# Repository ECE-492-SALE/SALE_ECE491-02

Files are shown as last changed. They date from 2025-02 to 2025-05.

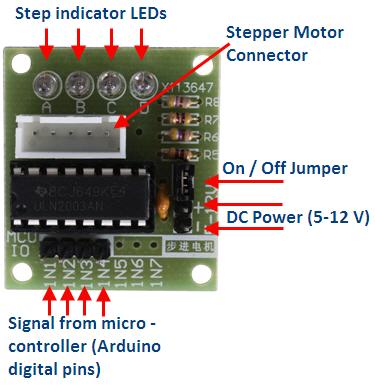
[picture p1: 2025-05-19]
Smart Pill Box/Schematic/UNL2003-board.jpg

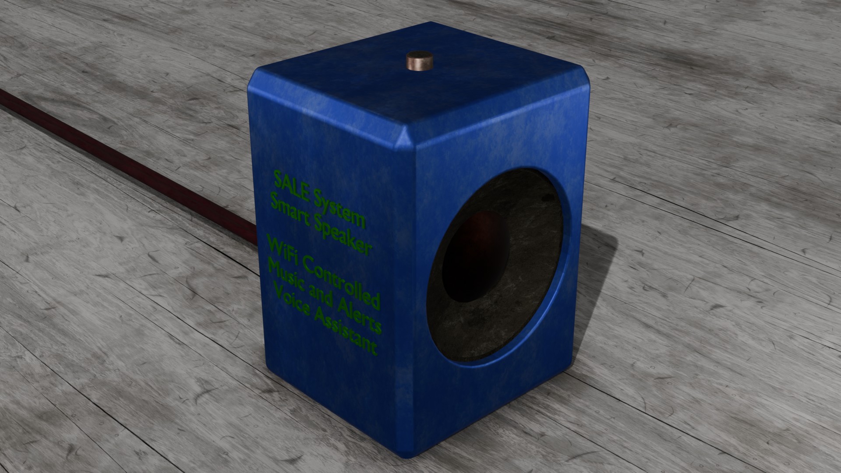
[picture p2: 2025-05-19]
SmartSpeaker/SmartSpeakerRender3.jpg

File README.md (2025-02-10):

# SALE_ECE491-02
Smart Assistive Living Environment (SALE) Senior Design project at Lafayette College

## Setup

### If you're downloading this on a new device, follow these steps

Open a Developer PowerShell from the Start Menu using the Start->All apps- >Raspberry Pi Pico SDK v1.5.5->Pico – Developer PowerShell I also suggest that you right-click on this menu entry and select “Pin to Start” for faster access in the future.

cd into your Documents folder

Run the following commands:
```bash
mkdir pico
cd pico
git clone -b master https://github.com/raspberrypi/pico-sdk.git
cd pico-sdk 
git submodule update --init 
cd .. 
git clone -b master https://github.com/raspberrypi/pico-examples.git
git clone https://github.com/priskillaw/SALE_ECE491-02.git
```

## Before making any changes, follow these steps

Open a Developer PowerShell 

cd into SALE_ECE491-02

Run "git pull"

You can start working now. Open Pico - Visual Studio Code

## To run things
```bash
cd build 
cmake -G "NMake Makefiles" .. 
nmake
```

Reboot the pico, then drag and drop the .uf2 file from the build file into the pico in file explorer

## To push things
cd into SALE_ECE491-02
```bash
git add Folder_Name
git commit -m "message/notes"
git push
```

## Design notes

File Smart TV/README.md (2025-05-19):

# Setting up the Smart TV

These instructions assume you already have a Roku set up on your TV.

1. Follow the steps in the [Getting started with your Raspberry Pi Pico W](https://projects.raspberrypi.org/en/projects/get-started-pico-w/0) guide to:
   - Install MicroPython onto the Pi Pico W
   - Set up the Thonny Python IDE

2. Download [`main.py`](https://github.com/ECE-492-SALE/SALE_ECE491-02/blob/main/Smart%20TV/main.py).

3. Open main.py in Thonny and edit the **Internet Credentials** section in the code to include:
   - Your Wi-Fi credentials
   - Your Roku device's IP address

4. Save the modified program to your Pico:
   - Go to `File` > `Save As` > `Raspberry Pi Pico`
   - Ensure the file name is exactly `main.py`
   - You may need to overwrite the existing `main.py` file

> **Note:** Naming the file `main.py` ensures the program starts automatically when the Pico receives power.

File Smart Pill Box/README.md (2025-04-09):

# Raspberry Pi Pico W Home Assistant Starter Project Using `arduino-pico`

I'm pretty excited about Pico W: it's such a reliable, high-quality board and each one costs just $6 (if you can find one).

I'm building an IoT project with Pico W and Home Assistant, and it took weeks of research and experimentation to figure out the basics of integration of all the necessary components. This starter pulls together everything I've learned so you can get to building quickly.

Fill out `src/Credentials.h`, upload to your Pico W, then you'll have a working integration that allows you to toggle the Pico W's board LED from the Home Assistant dashboard. From this starter you'll have a solid foundation to build your own custom device in a private, local Intranet of Things.



This readme will provide pointers to everything you'll need. Let me know if it's missing anything!

## Dependencies

- [Raspberry Pi Pico W](https://www.raspberrypi.com/products/raspberry-pi-pico/?variant=raspberry-pi-pico-w), a $6 microcontroller board with WiFi
- [PlatformIO](https://platformio.org/platformio-ide), an extension for [VSCode](https://code.visualstudio.com) with the most robust and reliable Arduino developer experience
- [`arduino-pico`](https://github.com/earlephilhower/arduino-pico): a community-developed Arduino core for Pico/Pico W and other RP2040 boards with constant updates and excellent support for existing Arduino code
- [`arduino-home-assistant`](https://github.com/dawidchyrzynski/arduino-home-assistant): a thorough Arduino/Home Assistant integration using MQTT

## Getting started

---
### Prerequisites
- PlatformIO set up in VSCode
- Home Assistant and MQTT broker accessible on the WiFi network your Pico W is joining (see appendix below for guidance on setup)
- HA MQTT integration with discovery enabled (this is the default/recommended behavior, so unless you turned it off, you're probably good to go)
---

1. Hold the `BOOTSEL` button on your Pico W while connecting it via USB
2. Open this project in VSCode
3. Edit `src/Credentials.h` with:
```
  - WiFi SSID
  - WiFi Password
  - MQTT Username
  - MQTT Password
  - MQTT Broker IP
```
4. Select the PlatformIO sidebar tab and choose Project Tasks > Upload and Monitor
5. Once the project logs a connection to the MQTT broker, open your Home Assistant instance
6. From Settings > Devices and Services, find the MQTT card and click the link that says `X devices`
7. From the resulting list, select `Pico W HA Starter`
8. Under the **Controls** heading you should see `Board LED`. Toggle the switch to turn your green board LED on and off



That's it. Now you've got a working example integration of all the pieces needed to communicate between an inexpensive, high-quality microcontroller and Home Assistant, all happening on your local network.

See the [examples in `arduino-home-assistant`](https://github.com/dawidchyrzynski/arduino-home-assistant/tree/main/examples) for additional components you can easily integrate, including sensors, buttons, even HVAC controls.

# Troubleshooting

- To come

# Appendix: Setting up a local Home Assistant installation with Mosquitto

## Home Assistant install

Home Assistant can be [installed](https://www.home-assistant.io/installation/) several ways on all kinds of hardware. Raspberry Pi is a popular choice, but you can also use your existing computer for initial explorations. *Home Assistant Container* is probably the quickest and most portable way to get started, whichever hardware you're using, though this does mean you'll have to manage some add-ons yourself, including MQTT.

## MQTT and Mosquitto

MQTT provides realtime messaging between devices in a network. The [Eclipse Mosquitto](https://github.com/eclipse/mosquitto) project offers a server that can act as an _MQTT broker_, a central hub for MQTT devices to send and receive data.

If you're using **Home Assistant Operating System**, check these instructions to [install the Mosquitto MQTT broker add-on](https://github.com/home-assistant/addons/blob/master/mosquitto/DOCS.md).

If you're using **Home Assistant Container**, [this tutorial](https://hometechhacker.com/mqtt-home-assistant-using-docker-eclipse-mosquitto/) provides a great overview on how to set up and secure Mosquitto in a seperate container.

Once your MQTT broker is enabled, [add the MQTT integration to your Home Assistant instance](https://www.home-assistant.io/integrations/mqtt/).

# Pull requests

PRs are welcome on these points:

- Enhance documentation (especially any troubleshooting steps you found helpful)
- Refine project structure
- Additional code paths to accommodate common variations (unsecured MQTT broker, different WiFi authentication, etc)
- Fix my bad C++

The goal of the project is to provide enough example structure to allow developers to add complexity without making a messy, crowded `main.cpp` file. PRs that simplify down to a single file probably won't be merged. If you have ideas on how to make this an even better foundation for building complex IoT projects, I'm all ears.

---

Questions? Comments? Gripes? Open an [issue](https://github.com/daniloc/PicoW_HomeAssistant_Starter/issues/new/choose) if you think there will be general interest or impact on the project. Otherwise hit me up: [mail@danilocampos.com](mailto:mail@danilocampos.com).

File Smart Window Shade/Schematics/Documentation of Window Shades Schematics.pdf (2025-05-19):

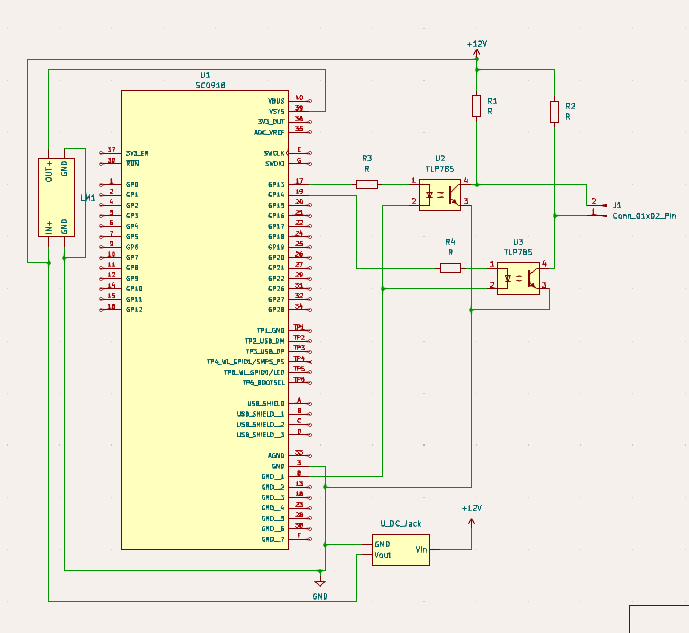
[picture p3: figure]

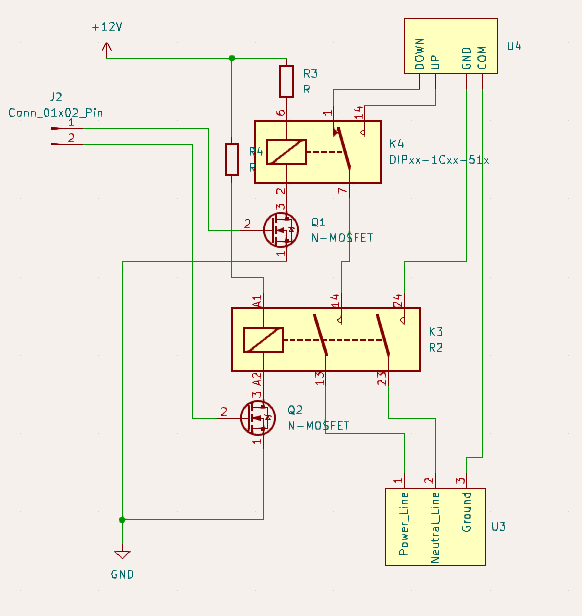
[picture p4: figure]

New Revisions made 02/09/2025: Changed layout of power distribution from the 12 to 5 volt converter.

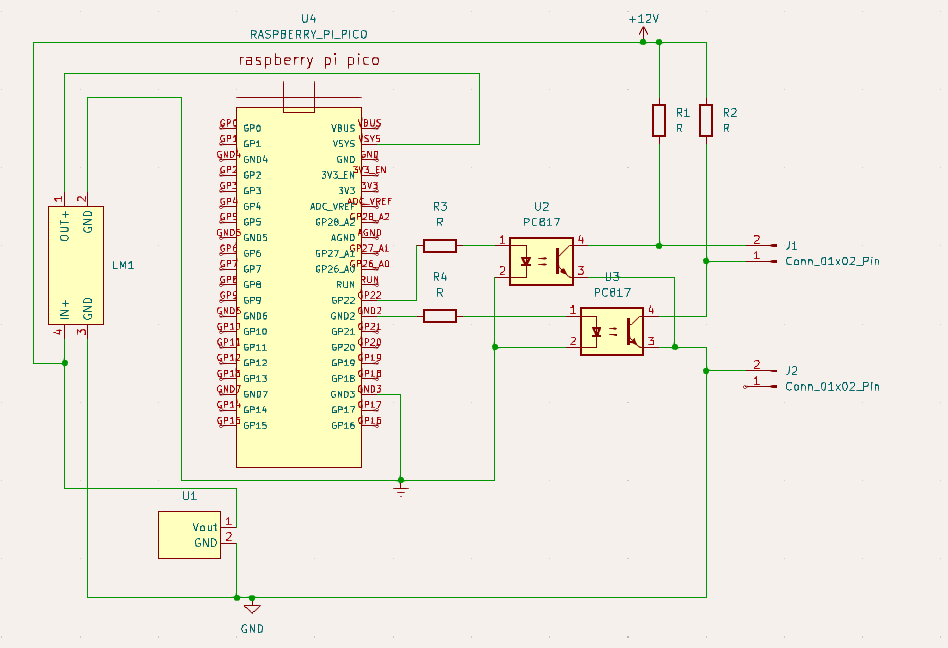
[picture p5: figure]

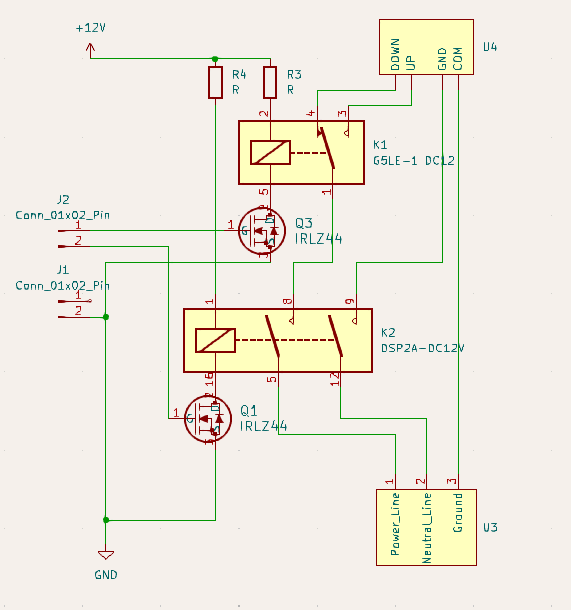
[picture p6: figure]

New revisions made 02/12/2025: Adjusted resistors to one schematic from the other, switched transistors, and fixed schematic layout. The resistors in this schematic are as follows: R1=180k, R2=200k, R3 & R4 = 10k.

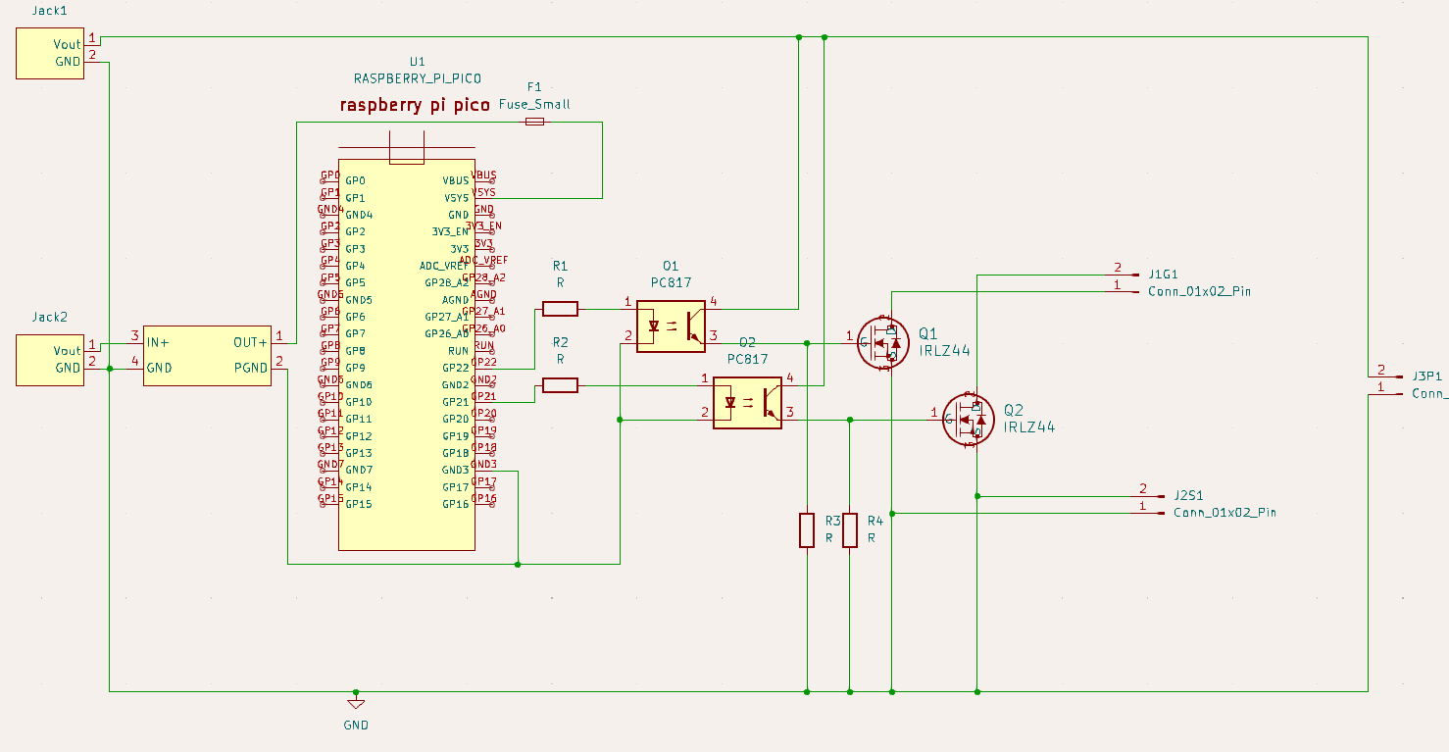
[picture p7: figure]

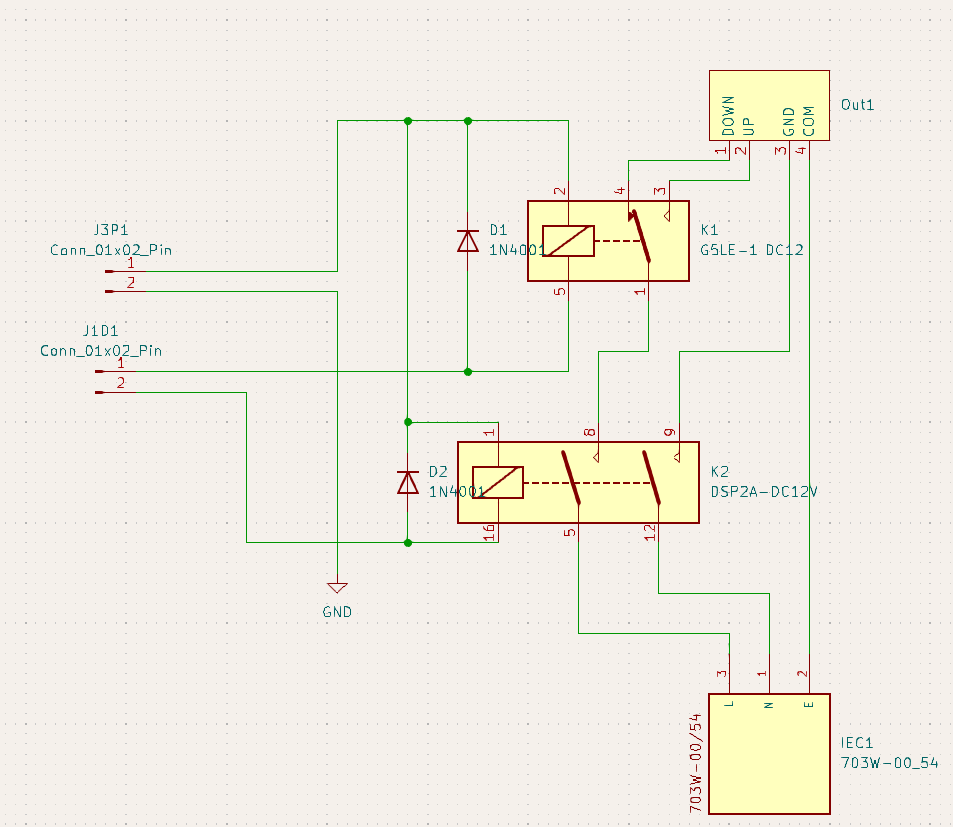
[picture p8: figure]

New revisions made 02/15/2025: Adjusted placement of resistors and their values as follows: R3=180k, R4=200k, R1 & R2 = 10k. Also, implemented fly back diodes to prevent unwanted voltage spikes.

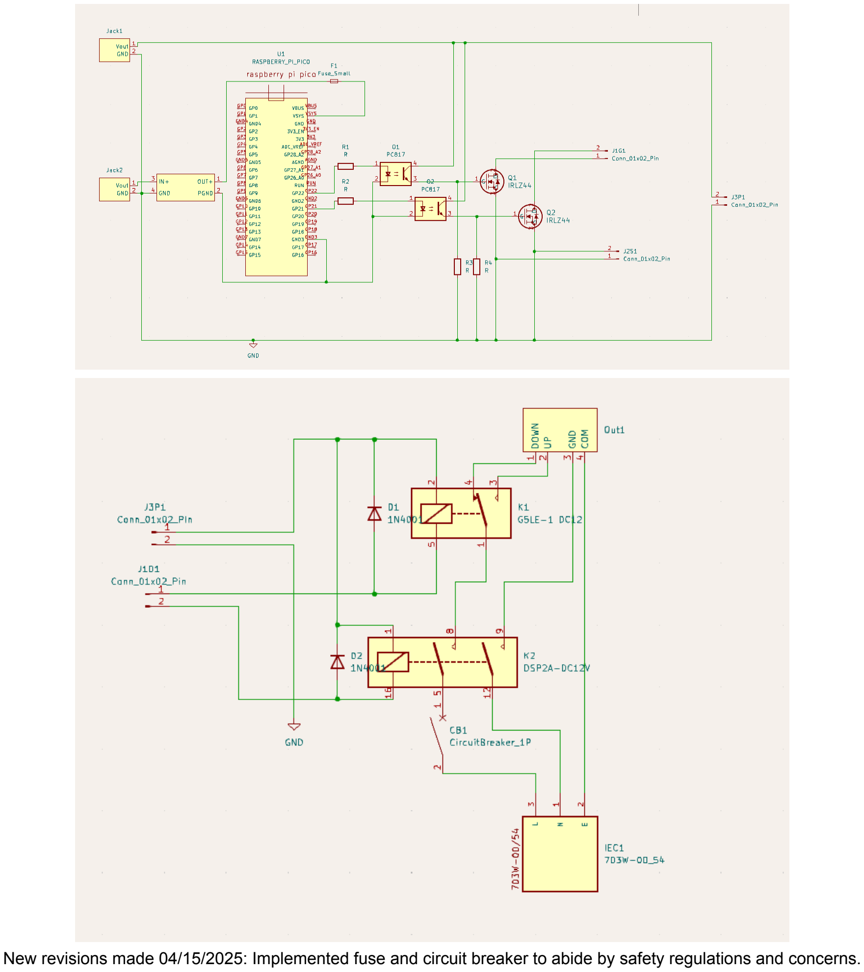
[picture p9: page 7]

New revisions made 04/15/2025: Implemented fuse and circuit breaker to abide by safety regulations and concerns.

The system design is divided across two separate PCBs: one dedicated to power distribution and the other to the microcontroller. This separation provides electrical isolation between the DC power and AC power domains, enabling safe and effective motor control. The Raspberry Pi Pico W microcontroller communicates with the central hub using the MQTT protocol, facilitated by the ArduinoHA library. This allows the device to be controlled through the Home Assistant (HA) web interface.

Wiring:

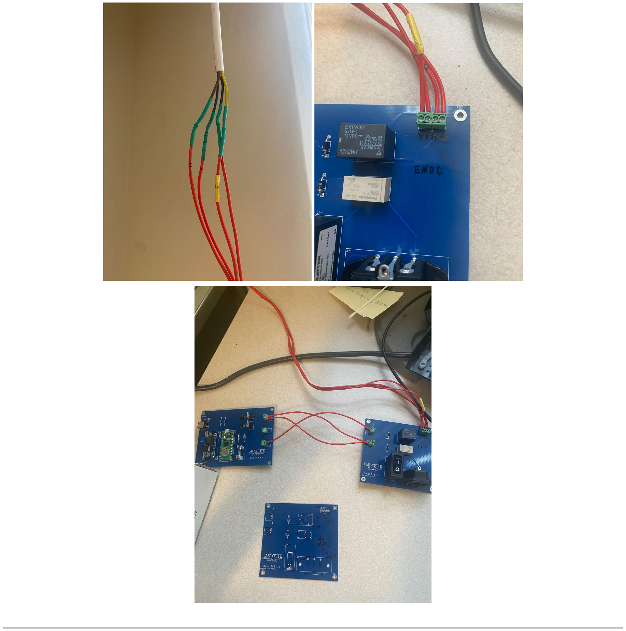
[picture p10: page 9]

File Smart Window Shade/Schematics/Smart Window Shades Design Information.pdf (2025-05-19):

What is it?

The Smart Window Shades is a window shade controller that is designed for residents to control their window blinds through the kick buttons and a smart mobile device UI interface. The
window shade consists of various components, such as the motor, a PCB (high voltage) that controls power to the window shade control system, and another PCB (low voltage) that controls communication with the hub.

What is the structure?

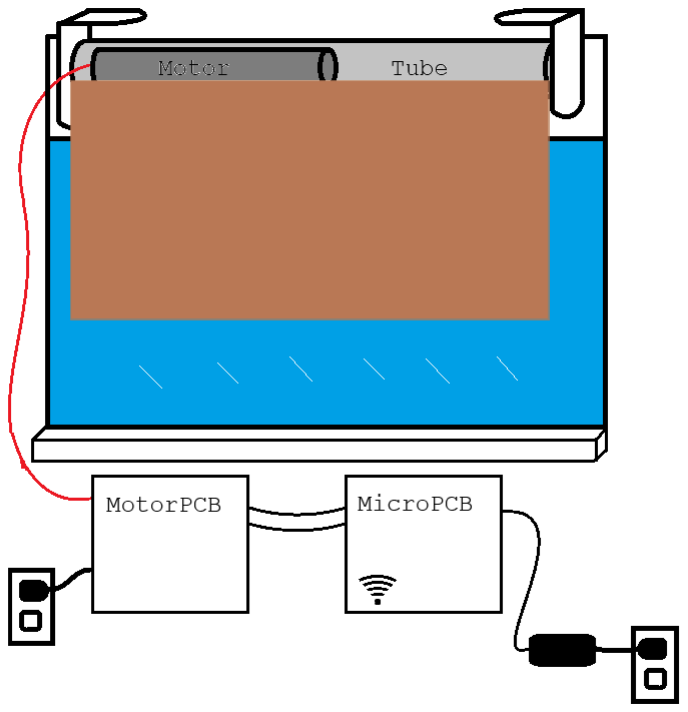
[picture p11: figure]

How does it work?

The main function of the device is to simply operate a motor up and down. It completes this function with the use of two PCBs, one with power distribution from a wall outlet and another with a microcontroller that will communicate with the hub and allow for control of the overall device. The power distribution PCB, or the MotorPCB, utilizes relays to switch on and off the motor as well as the direction of the motor, and hence the shades. Meanwhile, the MicroPCB uses DC 12V as power and sends signals to the MotorPCB through wired connections to switch the relays.

The microcontroller, Raspberry Pi Pico W, utilizes PlatformIO and C++ as the compiler and code language. The Pico W communicates with the hub through Wi-Fi using the MQTT protocol. It uses the ArduinoHA library to communicate automation functions with the HUB 1. (https://dawidchyrzynski.github.io/arduino-home-assistant/index.html)

Sources

1- ArduinoHA documentation- link (https://dawidchyrzynski.github.io/arduino-home-assistant/index.html)

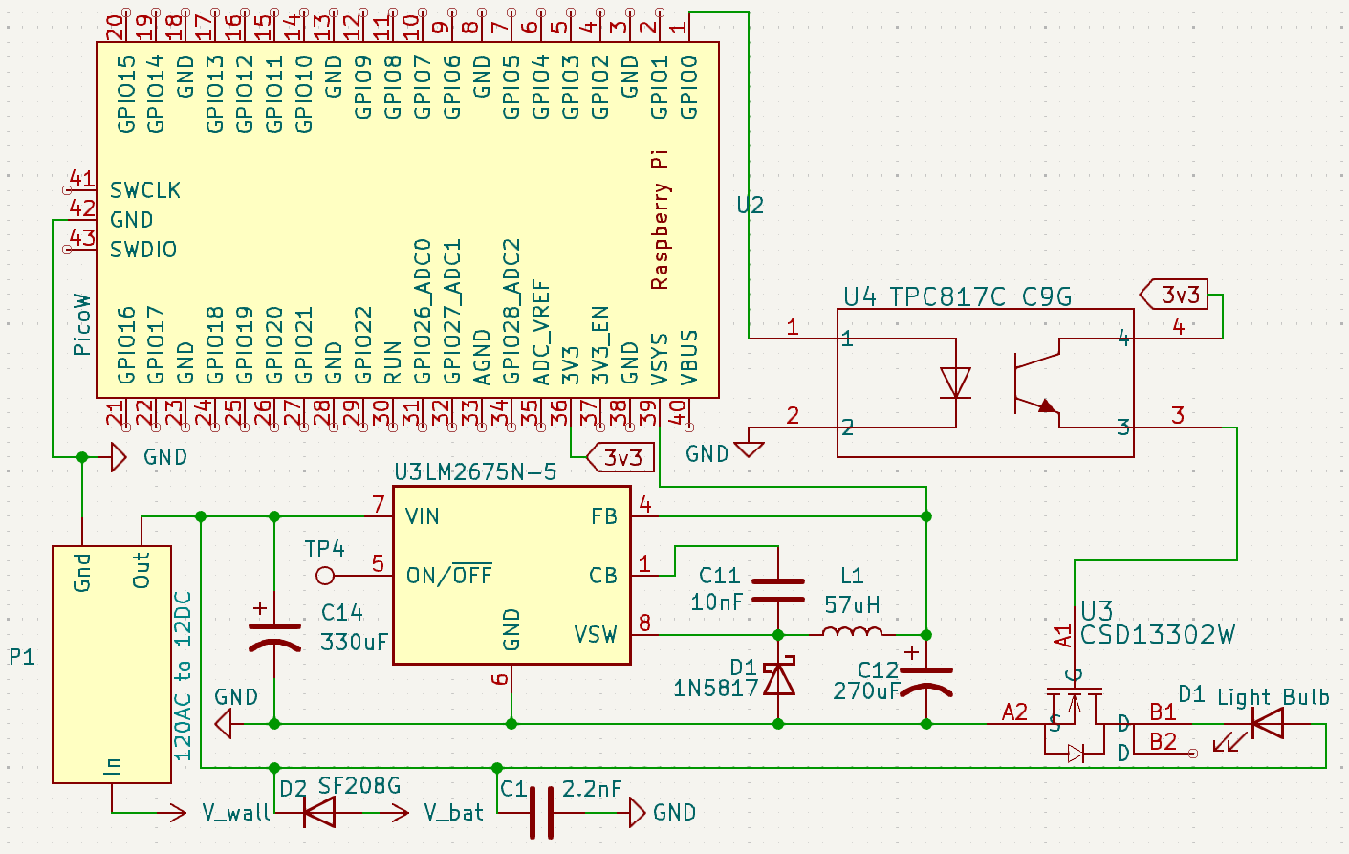
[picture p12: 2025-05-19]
Smart Light/Schematic/CircuitImage.png

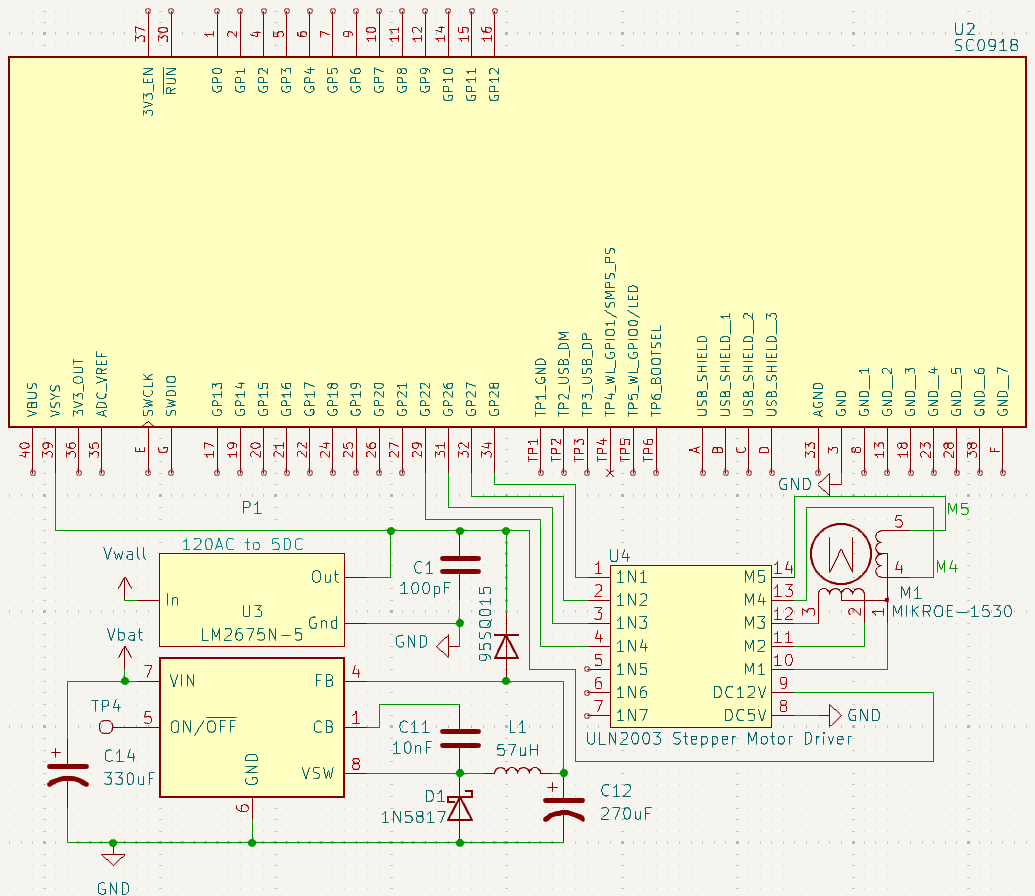
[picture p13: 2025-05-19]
Smart Pill Box/Schematic/CircuitImage.png

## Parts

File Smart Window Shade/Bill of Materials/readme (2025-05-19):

Please refer to the Window Shade Bill of Materials for money spent on device development.

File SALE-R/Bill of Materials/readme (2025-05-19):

Please refer to the SALE-R Bill of Materials for money spent on device development.

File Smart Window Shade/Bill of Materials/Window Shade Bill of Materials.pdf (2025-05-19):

Quantity | Cost Desc. | Part Number | Part Description | Link to Product | Per Unit | Total Per Item
1 | each | | 12V DC Adapter | https://www.amazon.com/Facmogu-Connector-5-5x2-5mm-5-5x2-1mm-Transformer/dp/B09BQBWKKT $14.39 | | $14.39
1 | each | | Power Cord | https://www.amazon.com/dp/B072BYGKZZ | $6.86 | $6.86
2 | each | 255-1052-ND | DSP2A-DC5V 5V Relay Non-Latch DPST-NO(2 Form A) | https://www.digikey.com/en/products/detail/panasonic-electric-works/DSP2A-DC5V/251824 $5.29 | | $10.58
2 | each | Z1014-ND | G5LE-1 DC5 5V Relay Non-Latch SPDT(1 Form C) | https://www.digikey.com/en/products/detail/omron-electronics-inc-emc-div/G5LE-1-DC5/280368 $1.84 | | $3.68
2 | each | 255-1053-ND | DSP2A-DC12V 12V Relay Non-Latch DPST-NO(2 Form A) | https://www.digikey.com/en/products/detail/panasonic-electric-works/DSP2A-DC12V/251825 $6.28 | | $12.56
2 | each | Z1015-ND | G5LE-1 DC12 12V Relay Non-Latch SPDT(1 Form C) | https://www.digikey.com/en/products/detail/omron-electronics-inc-emc-div/G5LE-1-DC12/280366 $1.70 | | $3.40
1 | each | | LM2596 Buck Converter | https://www.amazon.com/Maxmoral-Converter-Adjustable-Step-Down-Regulator/dp/B07MKQXNWG $7.99 | | $7.99
1 | pack of 10 | | DIP-4 PC817C PC817 opto isolator | https://www.amazon.com/MEETOOT-Transistor-Optocoupler-Mounting-Photoelectric/dp/B0BZY8NPLZ $4.99 | | $4.99
1 | each | 703W-00/54 | AC Power Entry Modules PCB | https://www.digikey.com/en/products/detail/qualtek/703W-00-54/245561 $2.02 | | 2.02
2 | each | 58-TIL197X-ND | TIL197X Optosiolator | https://www.digikey.com/en/products/detail/isocom-components-2004-ltd/TIL197X/21184649 $1.080 | | $2.160
2 | each | FOD852300-ND | FOD852300 Optoisolator | https://www.digikey.com/en/products/detail/onsemi/FOD852300/1054006 $1.140 | | $2.280
10 | each | WM7770-ND | 2 Position Terminal Block Header | https://www.digikey.com/en/products/detail/molex/0395021002/1280621 $0.459 | | $4.590
1 | each | | 120V Electric Tubular Motor for Roller Shades | https://www.ebay.com/itm/113835892439?chn=ps&norover=1&itemid=113835892439&targetid=4580771614098651&device=c&mktype=&googleloc=&poi=&campaignid=603247547&mkgroupid=1234752552191001&rlsatarget=pla-4580771614098651&abcId=9316119&merchantid=51291 $140.380 | | $140.380
1 | each | 486-1632-ND | 4435.0004. circuit breaker | https://www.digikey.com/en/products/detail/schurter-inc/4435-0004/1576911?s=N4IgTCBcDaICxwMwFYB0AGTcQF0C%2BQA $16.570 | | $16.570
10 | each | 1N4001 | Diode | https://www.digikey.com/en/products/detail/diotec-semiconductor/1N4001/13164614 $0.073 | | $0.730
10 | each | 486-1172-ND | 751.0062, Fuse Clip 10 A 1 Circuit Cartridge Through Hole | https://www.digikey.com/en/products/detail/schurter-inc/0751-0062/1522971?s=N4IgTCBcDaIAwHYCsBGAdHOA2CBdAvkA $0.219 | | $2.190
5 | each | 5923-5ST400-R-ND5ST 400-R, FUSE GLASS 400MA 250VAC 5X20MM | | https://www.digikey.com/en/products/detail/bel-fuse-inc/5ST-400-R/1009014 $0.346 | | $1.730
10 | each | 277-1721-ND | Screw Terminal (2 pos) | https://www.digikey.com/en/products/detail/phoenix-contact/1984617/950849 $0.620 | | $6.200
1 | set of 5 | | Hernan_Tovar-MicroPCB-Gerber Files | | $9.100 | $9.100
1 | each | | 50mm Tube | https://www.aliexpress.us/item/2255800674929877.html?spm=a2g0o.productlist.main.69.68243c481ZdaQA&algo_pvid=15d34c6a-c3b3-4ebb-8017-95513a388cc9&algo_exp_id=15d34c6a-c3b3-4ebb-8017-95513a388cc9-34&pdp_ext_f=%7B%22order%22%3A%2216%22%2C%22eval%22%3A%221%22%7D&pdp_npi=4%40dis%21USD%218.08%215.66%21%21%2158.06%2140.64%21%402103244417417945778375013e710d%2110000009689232526%21sea%21US%210%21ABX&curPageLogUid=lSyqkVcQup2B&utparam-url=scene%3Asearch%7Cquery_from%3A&gatewayAdapt=glo2usa $15.040 | | $15.040
1 | each | | 50mm Tube Aliexpress Shipping (88.5% ≤ 15 days) | | $25.200 | $25.200
1 | each | Window Shade Cloth - 8x12ft | https://www.amazon.com/Shatex-Fabric-Sun-Block-Pergola-Vertical/dp/B0152638SC?crid=1F482N8GGBAL4&dib=eyJ2IjoiMSJ9.0UGw9fhsERxLAzTZLdW-JWIaOosoAo99veP5jVaRUsiY2D-IYwChbElyhkwkbPCLwDlF8RiHA2zShFba4dmbsUE518HGo6yW3qHcKo2unuJsxlZyP4cbEDyOchVSCSaZ_oQqpo7o0g4_KozOwEVsKYBbmsE1sUZbhrxUdmricc5waIAYOgvM7MPXfemQZp8r2P_yj_VbM_mmKQ-Z8iuHsFjxTMo1GycocEaOXfID_1Qkm3uDPHZP1Ln6CnfGGQ0my2wNWTUSEMKE6iaxYibsJGw_EuJyJuGPgF2Owds7DlNpPoJbha8ORG1NZniMUqEv3o7y6jIYL9mhtwYntKwfBSfl49S7hAqa5w8ozXxaJbd4RB7oNQVJvZcE7Gi1dnUwq1M6zdff-pdXaC-OYXHisOYX2cvZJqxRhrCS96zi21_myYwA3JuHQC6_7cziRtPF.PTbvPzUGwK8BUv7smSho9WjuU2KZ9PW01qAZRnOhmMo&dib_tag=se&keywords=shade%2Bfabricroll&qid=1742962712&sprefix=shade%2Bfabricrol%2Caps%2C327&sr=8-16&th=1 $25.930 | $25.930
1 | each | Heat Shrink Kit | https://www.amazon.com/Ginsco-580-pcs-Assorted-Sleeving/dp/B01MFA3OFA $6.990 | $6.990
2 | each | Clear Scratch Acrylic Sheet, 12" x 12" x 5/64" | https://www.mcmaster.com/products/acrylic-plastic/plastic-1~/clear-scratch-and-uv-resistant-acrylic-sheets-and-bars/ $5.420 | $10.840
| | | Grand Total | $336.40

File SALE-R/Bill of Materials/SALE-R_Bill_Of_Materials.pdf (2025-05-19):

Quantity | Cost Desc. | Part Number | Part Description | Link to Product | Per Unit | Total Per Item
1 | group of 10 | Z12567-ND | Omron EESX3173 Optical Switch https://www.digikey.com/en/products/detail/omron-electronics-inc-emc-div/ee-sx3173-p2/9695331 $18.910 | | | $18.91
5 | each | Z8289-ND | Switch Cable | https://www.digikey.com/en/products/detail/omron-electronics-inc-emc-div/EE-5002-1M/8124128 (https://www.tti.com/content/ttiinc/en/apps/part-detail.html?partsNumber=EE-5002%201M&mfgShortname=OMR&msclkid=a04ac9077cad10313c51ae0e2bbb2bc2) $4.954 | | $4.95
5 | each | 497-4226-5-ND | Voltage Regulator | https://www.digikey.com/en/products/detail/stmicroelectronics/L7805ABP/725181?utm_adgroup=Integrated%20Circuits&utm_source=bing&utm_medium=cpc&utm_campaign=Dynamic%20Search_EN_RLSA&utm_term=integrated%20circuits&utm_content=Integrated%20Circuits&utm_id=bi_cmp-384476624_adg-1299622969467348_ad-81226484852599_dat-2333026235351130:aud-807631101:loc-190_dev-c_ext-_prd-&msclkid=30f93d07fe0513298ca15a0ea9756c5f $1.260 | | $6.30
10 | each | 296-1391-5-ND | Op amp - LM324N | https://www.digikey.com/en/products/detail/texas-instruments/LM324N/277627 $0.238 | | $2.38
10 | each | 754-1615-ND | RGB LED - WP154A4SUREQBFZGC https://www.digikey.com/en/products/detail/kingbright/WP154A4SUREQBFZGC/3084119?utm_adgroup=&utm_source=google&utm_medium=cpc&utm_campaign=PMax%20Shopping_Product_Medium%20ROAS%20Categories&utm_term=&utm_content=&utm_id=go_cmp-20223376311_adg-_ad-__dev-c_ext-_prd-3084119_sig-CjwKCAjwmaO4BhAhEiwA5p4YLyAk4I2ltCuXI3pE9Z9ASIh5VV7s5-rz4vQWj1uRPWmAPOnopJJF7xoCr4cQAvD_BwE&gad_source=1&gclid=CjwKCAjwmaO4BhAhEiwA5p4YLyAk4I2ltCuXI3pE9Z9ASIh5VV7s5-rz4vQWj1uRPWmAPOnopJJF7xoCr4cQAvD_BwE $1.224 | | | $12.24
10 | each | BC548BTACT-ND | Transistor (NPN) - BC548BTA https://www.digikey.com/en/products/detail/onsemi/BC548BTA/4553029?utm_adgroup=&utm_source=google&utm_medium=cpc&utm_campaign=PMax%20Shopping_Product_Medium%20ROAS%20Categories&utm_term=&utm_content=&utm_id=go_cmp-20223376311_adg-_ad-__dev-c_ext-_prd-4553029_sig-CjwKCAjwmaO4BhAhEiwA5p4YL67t7TMbeoZEc35zGVffhJ3N9crvRZnu1P-3F3I7a8i8qWXRaVbQNBoCnBMQAvD_BwE&gad_source=1&gclid=CjwKCAjwmaO4BhAhEiwA5p4YL67t7TMbeoZEc35zGVffhJ3N9crvRZnu1P-3F3I7a8i8qWXRaVbQNBoCnBMQAvD_BwE $0.124 | | | $1.24
10 | each | 1727-4115-1-ND | AND Gate - 74LVC1G08GV,125 https://www.digikey.com/en/products/detail/nexperia-usa-inc/74LVC1G08GV-125/1231422?utm_adgroup=Integrated%20Circuits&utm_source=bing&utm_medium=cpc&utm_campaign=Dynamic%20Search_EN_RLSA&utm_term=integrated%20circuits&utm_content=Integrated%20Circuits&utm_id=bi_cmp-384476624_adg-1299622969467348_ad-81226484852599_dat-2333026235351130:aud-807631099:loc-190_dev-c_ext-_prd-&msclkid=98d76569372a198b0c1c0242ff174319 $0.089 | | | $0.89
1 | each | TO-1127CS | TO-1127CS - 302/304 Stainless Steel Torsion Springs | Century Spring… https://www.centuryspring.com/shop/to-1127cs | | $8.780 | $8.78
1 | each | TO-1052CS | TO-1052CS - 302/304 Stainless Steel Torsion Springs | Century Spring… https://www.centuryspring.com/shop/to-1052cs | | $16.520 | $16.52
1 | each | TO-5074LSCS | TO-5074LSCS - 302/304 Stainless Steel Torsion Springs | Century… https://www.centuryspring.com/shop/to-5074lscs | | $6.360 | $6.36
5 | each | N71179212 | Omron Electronic Components EE-5002 https://us.rs-online.com/product/omron-electronic-components/ee-5002-1m/71179212/ $5.620 | | | $5.62
2 | each | OPB355T | Optical Interrupter | https://www.digikey.com/en/products/detail/tt-electronics-optek-technology/OPB355T/1636794?s=N4IgTCBcDaIPIAUBCBmArGgKiAugXyA $4.130 | | $8.26
1 | each | SUNLU | SUNLU 3D Printer Filament 1.75mm, 1kg Spool, Transparent PLA https://www.amazon.com/SUNLU-Filament-Transparent-Dimensional-Accuracy/dp/B07ZNG4L9P $18.990 | | | $18.99
1 | set of 5 | PCB | Gerber_KB_2025_Kaushik_Padmanabh https://drive.google.com/file/d/1kJjDtBSBimDMkwyHZpLCwrizQ20GpJf3/view?usp=drive_link $11.200 | | | $11.20
1 | each | Foot Rest | Foot Rest | https://www.amazon.com/EHO-Footrest-Washable-Ergonomic-Position/dp/B0CDPNHPX1 $48.820 | | $48.82
5 | each | EE-5002 1M | Switch Cable | https://www.digikey.com/en/products/detail/omron-electronics-inc-emc-div/ee-5002-1m/8124128 $3.786 | | $18.93
10 | each | 754-1615-ND | RGB LED - WP154A4SUREQBFZGC https://www.digikey.com/en/products/detail/kingbright/WP154A4SUREQBFZGC/3084119 $1.760 | | | $17.60
10 | each | BC548BTACT-ND | Transistor (NPN) - BC548BTA https://www.digikey.com/en/products/detail/onsemi/BC548BTA/4553029 $0.162 | | | $1.62
4 | each | 1727-4115-1-ND | AND Gate - SN74LS08N | https://www.digikey.com/en/products/detail/texas-instruments/SN74LS08N/277279 $0.740 | | $2.96
15 | each | 277-1721-ND | Screw Terminal (2 pos) | https://www.digikey.com/en/products/detail/phoenix-contact/1984617/950849 $0.598 | | $8.97
15 | each | 277-1722-ND | Screw Terminal (3 pos) | https://www.digikey.com/en/products/detail/phoenix-contact/1984620/950850 $0.651 | | $9.77
1 | each | Pi Pico | Raspberry Pi Pico WH - Pico Wireless with Headers Soldered https://www.adafruit.com/product/5544 | | $7.000 | $7.00
1 | each | Wire 25FT | 20 Gauge 5 Conductor Electrical Wire 25FT https://www.amazon.com/Conductor-Electrical-Stranded-Extension-Automotive/dp/B0CFJWSHKD $16.990 | | | $16.99
| | | | | Grand Total | $255.30

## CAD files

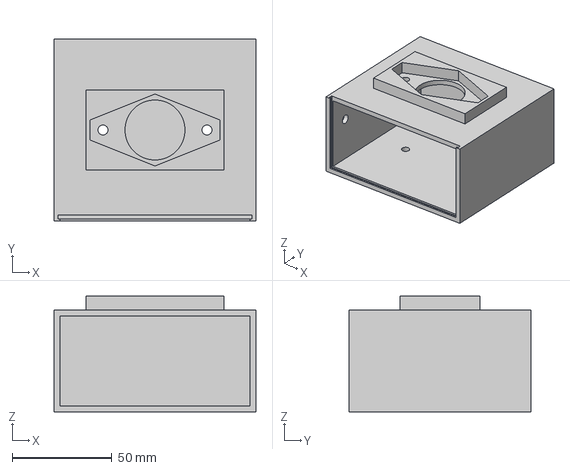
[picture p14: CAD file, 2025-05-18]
Smart Light/3D Print Files/carusoc_ece492_lighthousing.3mf
101.0 x 91.0 x 58.0 mm

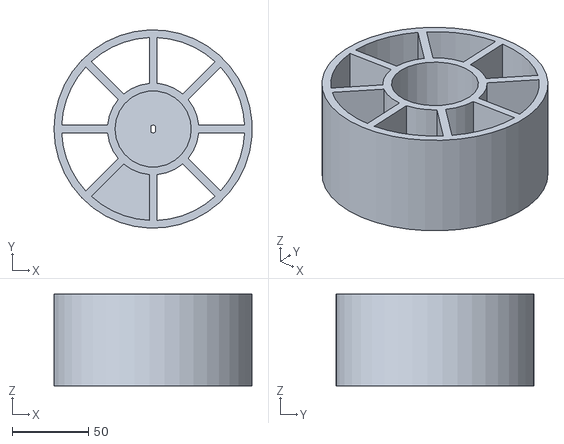
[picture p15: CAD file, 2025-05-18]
Smart Pill Box/3D Print Files/Pill+Box+Wheelv4.obj
129.8 x 129.9 x 60.0

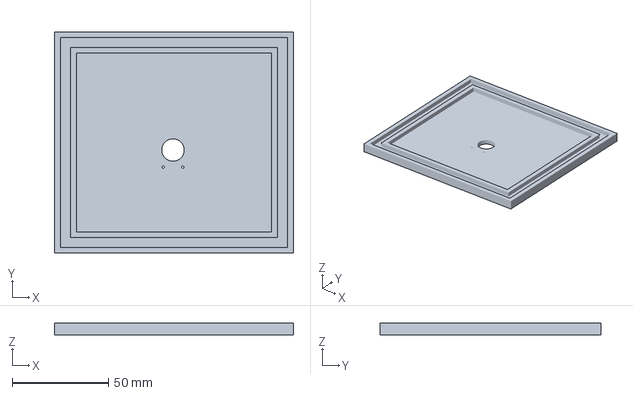
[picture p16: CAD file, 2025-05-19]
SmartSpeaker/3D Print Files/SmartSpeakerCaseTop.3mf
124.4 x 115.0 x 6.00 mm

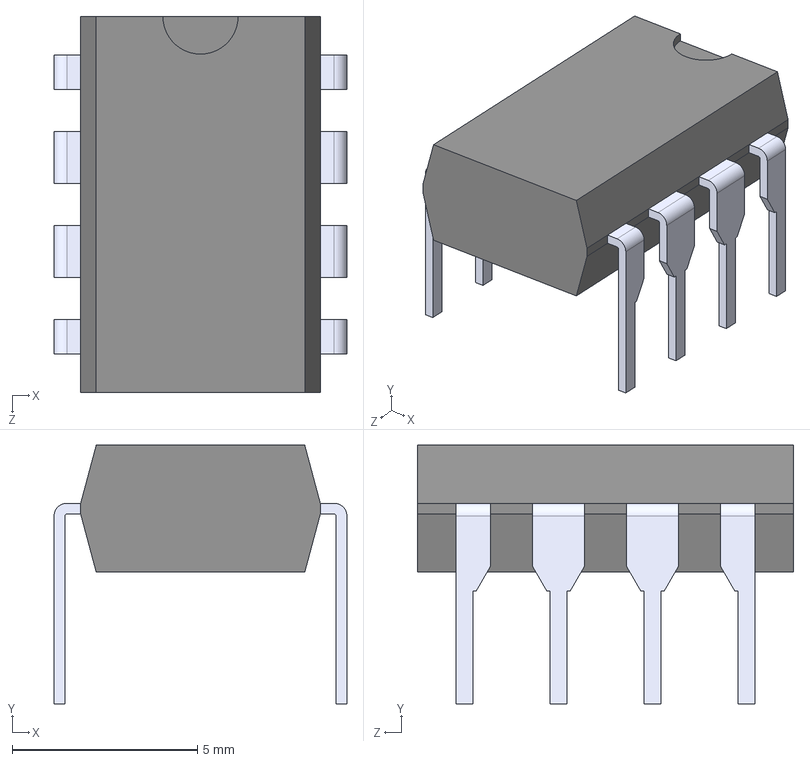
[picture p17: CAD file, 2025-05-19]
SmartSpeaker/Speaker/LTC1655CS8_TRPBF/LTC1655CN8_PBF.step
7.91 x 6.98 x 10.2 mm

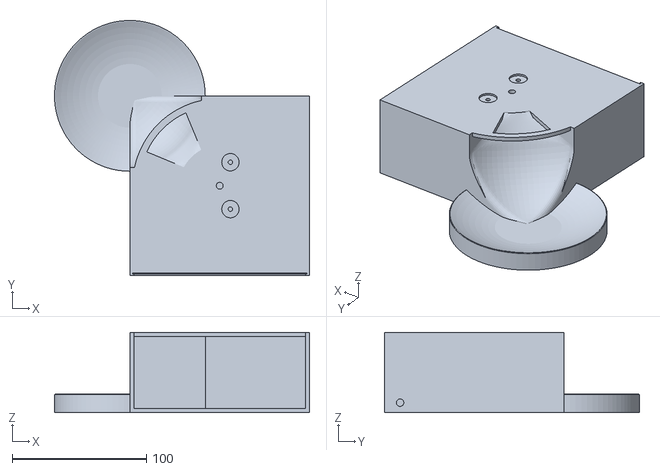
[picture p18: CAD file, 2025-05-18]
Smart Pill Box/3D Print Files/Pill Box Housing v3.stl
190.2 x 190.2 x 60.0

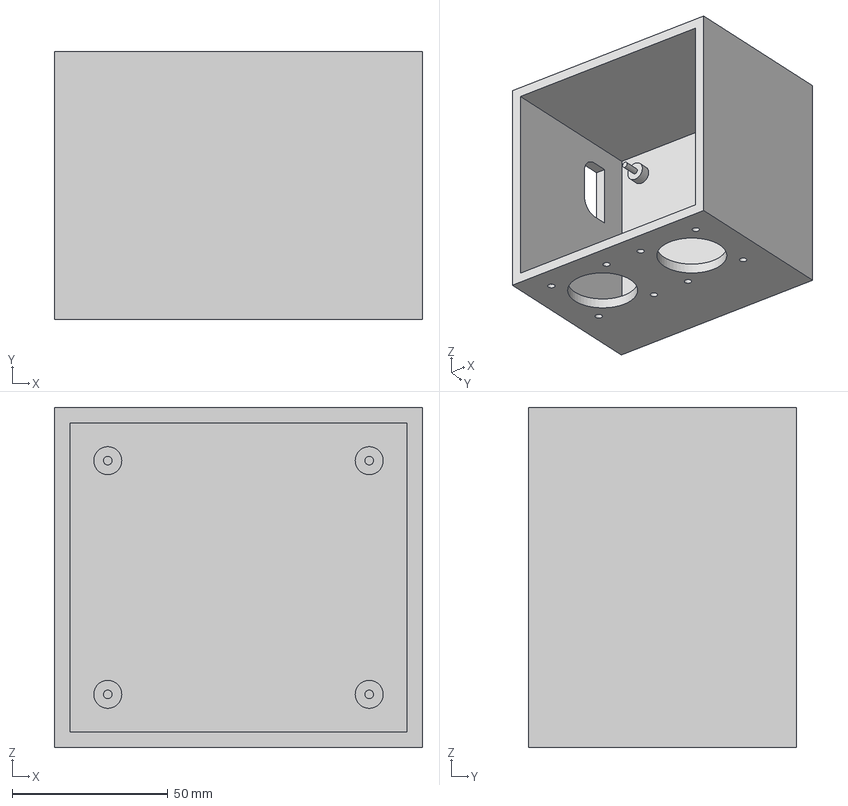
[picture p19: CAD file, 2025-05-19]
SmartSpeaker/3D Print Files/SmartSpeakerCase_Body.3mf
118.0 x 86.0 x 109.1 mm

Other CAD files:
SALE-R/3D Print Files/Bottom+V3.f3d
SALE-R/3D Print Files/Bottom+V4.f3d
SALE-R/3D Print Files/Hinge+Rods.f3d
SALE-R/3D Print Files/Kick-Button+Combined+Visual.f3z
SALE-R/3D Print Files/Top+V4.f3d
Smart Door/3D Print Files/Camera+Holder.f3d
Smart Window Shade/3D Print Files/Shades+PCB+Holder+#1.f3d
Smart Window Shade/3D Print Files/Shades+PCB+Holder+#2.f3d
SmartSpeaker/3D Print Files/speaker+structure+lid.f3d
SmartSpeaker/3D Print Files/speaker+structure.f3d

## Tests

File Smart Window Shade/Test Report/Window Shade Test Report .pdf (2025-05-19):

# Window Shade Test Report

############################################################################## Overall Summary: Window Shades are functional

Tested by: Hernan Tovar, Padmanabh Kaushik. Nicholas Sorak.
Date: 05/3/2025
Report Uploaded 5/19/20205 by Hernan Tovar-Molina ##############################################################################

Mechanical Design Requirements
Test T1: Interaction with Motor
- Equipment: Motor, relays, power supply, and wall outlet.
- Method: Apply a line voltage source switching via protoboard with relays attached, using 12 volts to switch on and off.
- Pass/Fail Criteria: Motor rotates once the voltage applied to the relays is high.

Test T2: Breaker Component
- Test Equipment: Built PCB, breaker.
- Test Method: Switch on/off the breaker component.
- Acceptance Criteria: Disables power to the motor, and motor doesn’t rotate.
Cover Requirements: Wired aspects shall be secured and out of reach/away from the resident.

Test T3: Window Shades Reach
- Test Equipment: Motor, built PCBs, shades.
- Test Method: Enable the motor to spin to its maximum, adjust as necessary.
- Acceptance Criteria: The shades reach to the bottom of the window.

Test T4: Accommodation of PCBs
- Test Method: Insert the PCBs into their designated 3d printed compartments. Check for proper fit, alignment, and secure positioning.
- Acceptance Criteria: The PCBs should fit securely within their housing, with no movement or obstruction.
- Test Equipment: 3D Fusion, ruler.

Cover Requirements: Wired aspects shall be secured and out of reach/away from the resident.

Electrical functionality
Test T5: Voltage Convertor Voltage Regulation
- Test Equipment: Digital multimeter or oscilloscope.
- Test Method:
- Measure the output voltage from the LM 2596 buck converter under both idle and active states.
- Repeat the test under different load conditions(turning the system on or off).
- Acceptance Criteria: The voltage supplied to the microcontroller output side should not exceed 5.1 V.

Test T6: Relay Circuit Current Limitation
- Test Equipment: Digital multimeter
- Test Method:
- Power the GPIO pins from the Pico W and measure the current flowing through the circuit under standard and maximum operating conditions.
- Measure the current in voltage across the drain and source from each transistor and calculate the current.
- Acceptance Criteria: The coil current in the Relays should be ≤ 25 mA and ≤ 33.3 mA, for the DSP2A-DC12V and the G5LE-1 DC12, respectively in all tested conditions.

Test T7: GPIO Input Voltage Limitation to Microcontroller
- Test Equipment: Digital multimeter or oscilloscope.
- Test Method:
- Measure the voltage at the GPIO input pin on the microcontroller in both idle and active states.
- Test under various input signal conditions to ensure stability.
- Acceptance Criteria: The voltage at the GPIO input should not exceed 3.8 V.

Wi-Fi Integration Functionality:

Test T8: Microcontroller Readings
- Test Equipment: Computer and Oscilloscope.
- Test Method:
- Verify if the name of the device appears on the console of the Hub.
- Monitor one of the GPIO pins on the microcontroller while the up cover option from the Home Assistant is pressed.
- Program the microcontroller to turn on the built-in LED if the button is pressed.
- Acceptance Criteria: The microcontroller should register a logic high or logic low signal depending on when the up or down, and stop is pressed.
Cover Requirements: Smart Window Shades shall be connected with the Smart Hub wirelessly.

System level integration (involves 5 buttons):

Setup:
- Attached the motor and tube with shades to the ceiling.
- Wired and connected both of the PCBs to power and each other.

Test T9: Control from HA website.
- Test Equipment: Computer
- Test Method: Use the Home Assistant website to control the shades
- Press either up or down arrows and the stop buttons.
- Acceptance Criteria: Window shades respond accordingly and further verified with audio feedback from the relay.
Test T10: Control from SMD interface.
- Test Equipment: Smart Mobile Device
- Test Method: Use the user interface on the SMD to control the shades.
- Press the arrows, up or down and stop.
- Acceptance Criteria: Window shades respond accordingly and further verified with audio feedback from the relay.
Test T11: Control from SALE-Remote buttons.
- Test Equipment: Kick Buttons

- Test Method: Navigate the user interface on the SMD by using the kick buttons to control the shades.
- Press the respective kick buttons; up, down or stop.
- Acceptance Criteria: Window shades respond accordingly and further verified with audio feedback from the relay.
T9-T11_Cover Requirements:
- The resident shall be able to raise/lower the Smart Window Shades by interfacing with the Smart Mobile Device.
- Simple controls; with a push/touch shall open or close.

Test Result Summary

Test No. | Pass/Fail
T1 | Pass
T2 | Pass
T3 | Pass
T4 | Pass
T5 | Pass
T6 | Pass
T7 | Pass
T8 | Pass
T9 | Pass
T10 | Pass
T11 | Pass

##################################End of report################################

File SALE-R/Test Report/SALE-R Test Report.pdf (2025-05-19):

# SALE-R Test Report

##################################################################################### Overall Summary: Kick Buttons are fully functional

Tested by: Padmanabh Kaushik, Nick Sorak, Scott Torzewski
Date: 5/1/2025
Report Uploaded: 5/19/2025 by Padmanabh Kaushik #####################################################################################
- Mechanical Design Requirements
- Test T1: Interaction with Optical Switch Surface (T1)
i. Method: Visually inspect and measure the clearance between the metal strap and the surface of the optical switch in all button positions using a caliper or other precision measuring tool.
ii. | Acceptance Criteria: There should be a minimum clearance of 1 mm between
| the metal strap and the optical switch surface in both pressed states.
iii. | Observation from Test: The clearance was 2mm between the strap and the
| optical switch, for buttons in the compressed state.
iv. | Pass/Fail: Pass
- Test T2: Laser Interruption upon Button Press (T2)
i. Method: Press the button and observe the optical switch output using a voltmeter
| to confirm that the laser is interrupted by the metal strap.
ii. | Acceptance Criteria: The laser should be fully interrupted once the button is
| pressed.
iii. | Observation from Test: The laser is fully interrupted when the button is pressed,
| as voltage goes down to 0V.
iv. | Pass/Fail: Pass
- Test T3: Laser Continuity in Equilibrium Position (T3)
i. Method: Place the button in its equilibrium position and monitor the optical
| switch output using a voltmeter.
ii. | Acceptance Criteria: The laser should remain uninterrupted in the unpressed
| state.
iii. | Observation from Test: The voltage does not change across the optical switch
| circuit when the button is not pressed.
iv. | Pass/Fail: Pass
- Test T4: Button Return to Equilibrium Position (T4)

i. Method: Manually press the button multiple times and observe whether it reliably returns to its original position. Use a caliper if needed to confirm alignment.
ii. | Acceptance Criteria: The button must return to its equilibrium position after
| every press.
iii. | Observation from Test: The button returns to its original position.
iv. | Pass/Fail: Pass
- Test T5: LED Circuitry Accommodation (T5)
i. Method: Insert the LED driving circuitry into its designated compartment and
| check for secure fit and unobstructed placement.
ii. | Acceptance Criteria: The circuitry must fit securely within the button housing
| with no movement or interference.
iii. | Observation from Test: The LED board fits properly within the button. Each
| LED circuit has dimensions of 2cm x 3cm.
iv. | Pass/Fail: Pass
- Electrical Functionality
- Test T6: Optical Switch Voltage Regulation (T6)
i. Method: Use a multimeter or oscilloscope to measure voltage supplied by the
| Buck Convertor regulator to the optical switch in both idle and active states,
| under various load conditions.
ii. | Acceptance Criteria: Voltage must not exceed 5.5 V.
iii. | Observation from Test: TThe output voltage was 5.2 V.
iv. | Pass/Fail: Pass
- Test T7: LED Driver Circuit Current Limitation (T7)
i. Method: Power the LED circuit and measure current across the 300-ohm source
| resistor using a multimeter. Test under standard and maximum base current
| conditions.
ii. | Acceptance Criteria: Current must remain ≤ 40 mA in all tested conditions.
iii. | Observation from Test: The maximum observed current per button was 38mA..
iv. | Pass/Fail: Pass
- Test T8: GPIO Input Voltage Limitation to Microcontroller (T8)
i. Method: Measure voltage at the GPIO input pin during idle and active states
| using a multimeter or oscilloscope.
ii. | Acceptance Criteria: Voltage must not exceed 3.8 V.
iii. | Observation from Test: The voltage at GPIO was 3.29 V.
iv. | Pass/Fail: Pass
- Individual Button Functionality
- Test T9: Microcontroller Readings (T9)
i. Method: Monitor GPIO pin on the microcontroller while pressing the button.
| The onboard LED should be programmed to turn on when a high signal is
| received.

ii. | Acceptance Criteria: The microcontroller must detect a logic high when the
| button is pressed.
iii. | Observation from Test: The microcontroller detects logic high when button is
| pressed.
iv. | Pass/Fail: Pass
- Test T10: LED Illumination on Button Press (T10)
i. Method: Press the button and visually verify that the button’s LED lights up and
| remains on while pressed.
ii. | Acceptance Criteria: LEDs must illuminate immediately when the button is
| pressed.
iii. | Observation from Test: LED lights up immediately when button is pressed.
iv. | Pass/Fail: Pass
- Test T11: Bluetooth Message Transmission on Button Press (T11)
i. Method: Pair the microcontroller with a tablet or computer. Monitor the
| receiving application or terminal to confirm transmission of
| “buttonName_Pressed” and default “buttonName_!Pressed” messages.
ii. | Acceptance Criteria: An “buttonName_Pressed” message must be sent when
| the button is pressed. “buttonName_!Pressed” must be sent when no button is
| pressed.
iii. | Observation from Test: The button press messages were transmitted properly,
| and were verified by displaying them on smart Mobile Device.
iv. | Pass/Fail: Pass
- System Level Integration (involves 5 buttons)
- Setup:
i. Power the button system (5 buttons and the circuitry) using a 12 V supply
ii. | Place the 5 buttons on a custom mount/footrest that is comfortable to use when a
| person is in a wheelchair.
- Test T12: Button State Detection and String Composition (T12)
i. Test Method: Use a USB connection to print serial output from the
| microcontroller while pressing each button individually and in combinations;
| confirm that the generated string accurately reflects the state of each button.
ii. | Acceptance Criteria: The generated string accurately reflects the current state of
| each button in the format "ON_1 OFF_2…" etc.
iii. | Observation from Test:.The generated string accurately reflected the current
| state of each button in the format "ON_1 OFF_2…" etc.
iv. | Pass/Fail: Pass
- Test T13: Bluetooth Transmission of Button States (T13)
i. Test Method: Pair a tablet or computer with the microcontroller via Bluetooth,
| then press buttons individually and in combinations while monitoring the
| received string in a logging application; verify that each transmission matches the
| current button states and test for consistency under rapid presses.

ii. | Acceptance Criteria: The tablet consistently receives the correct button state
| string for every combination of presses, in the specified format (e.g., Left
| pressed, Right pressed, etc.).
iii. | Observation from Test:. The button presses were detected in tight format. For
| instance Left pressed when the left button was pressed and vice versa..
iv. | Pass/Fail: Pass
- Test T14: Stability and Responsiveness Testing (T14)
i. Test Method: Use logging software to monitor transmitted strings while rapidly
| pressing buttons in different sequences, including simultaneous inputs; observe
| whether the system consistently updates the string without missing or
| misreporting button states.
ii. | Acceptance Criteria: The system should not miss any button press events or
| provide incorrect button states
iii. | Observation from Test: The system detects buttons pressed properly, even when
| they are pressed pretty fast. This is valid as long as button presses are within 0.25
| sec, which is the sampling time programmed in the controller.
iv. | Pass/Fail: Pass
| Test Result Summary

####################################End of Report####################################

Test No. | Pass/Fail
T1 | Pass
T2 | Pass
T3 | Pass
T4 | Pass
T5 | Pass
T6 | Pass
T7 | Pass
T8 | Pass
T9 | Pass
T10 | Pass
T11 | Pass
T12 | Pass
T13 | Pass
T14 | Pass

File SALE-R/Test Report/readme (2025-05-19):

Please see test report for details.
Tests perfromed by Padmanabh kaushik, Scott Torzewski, Nicholas Sorak

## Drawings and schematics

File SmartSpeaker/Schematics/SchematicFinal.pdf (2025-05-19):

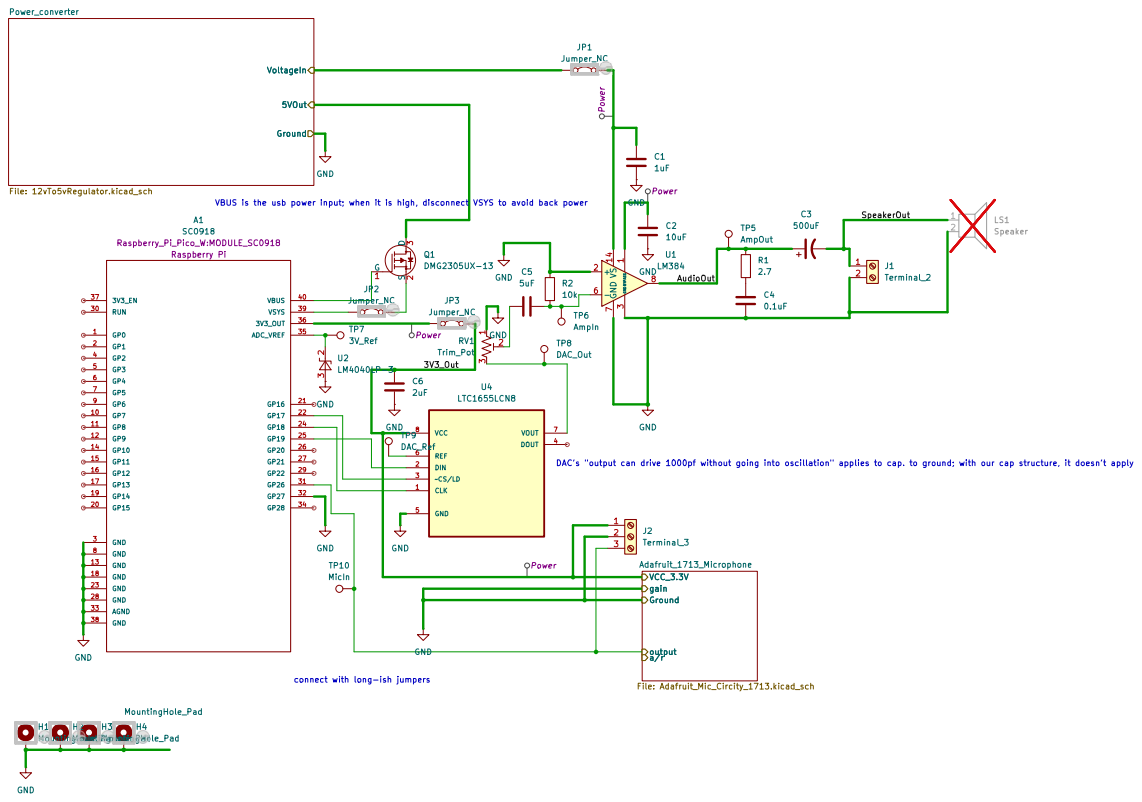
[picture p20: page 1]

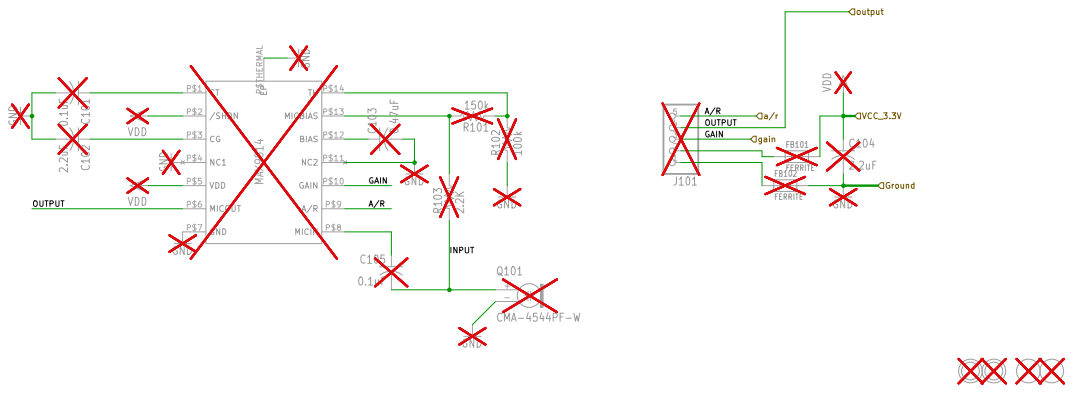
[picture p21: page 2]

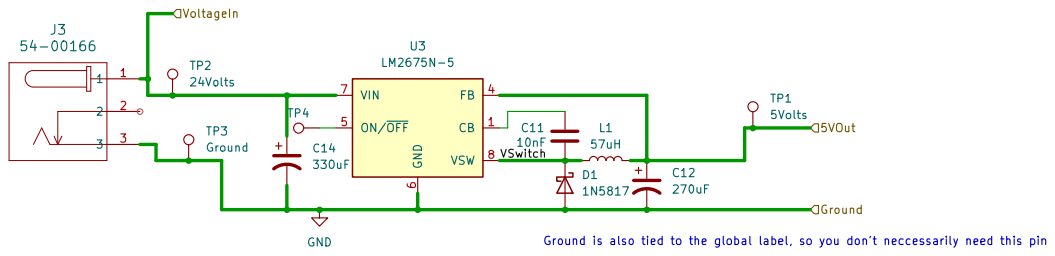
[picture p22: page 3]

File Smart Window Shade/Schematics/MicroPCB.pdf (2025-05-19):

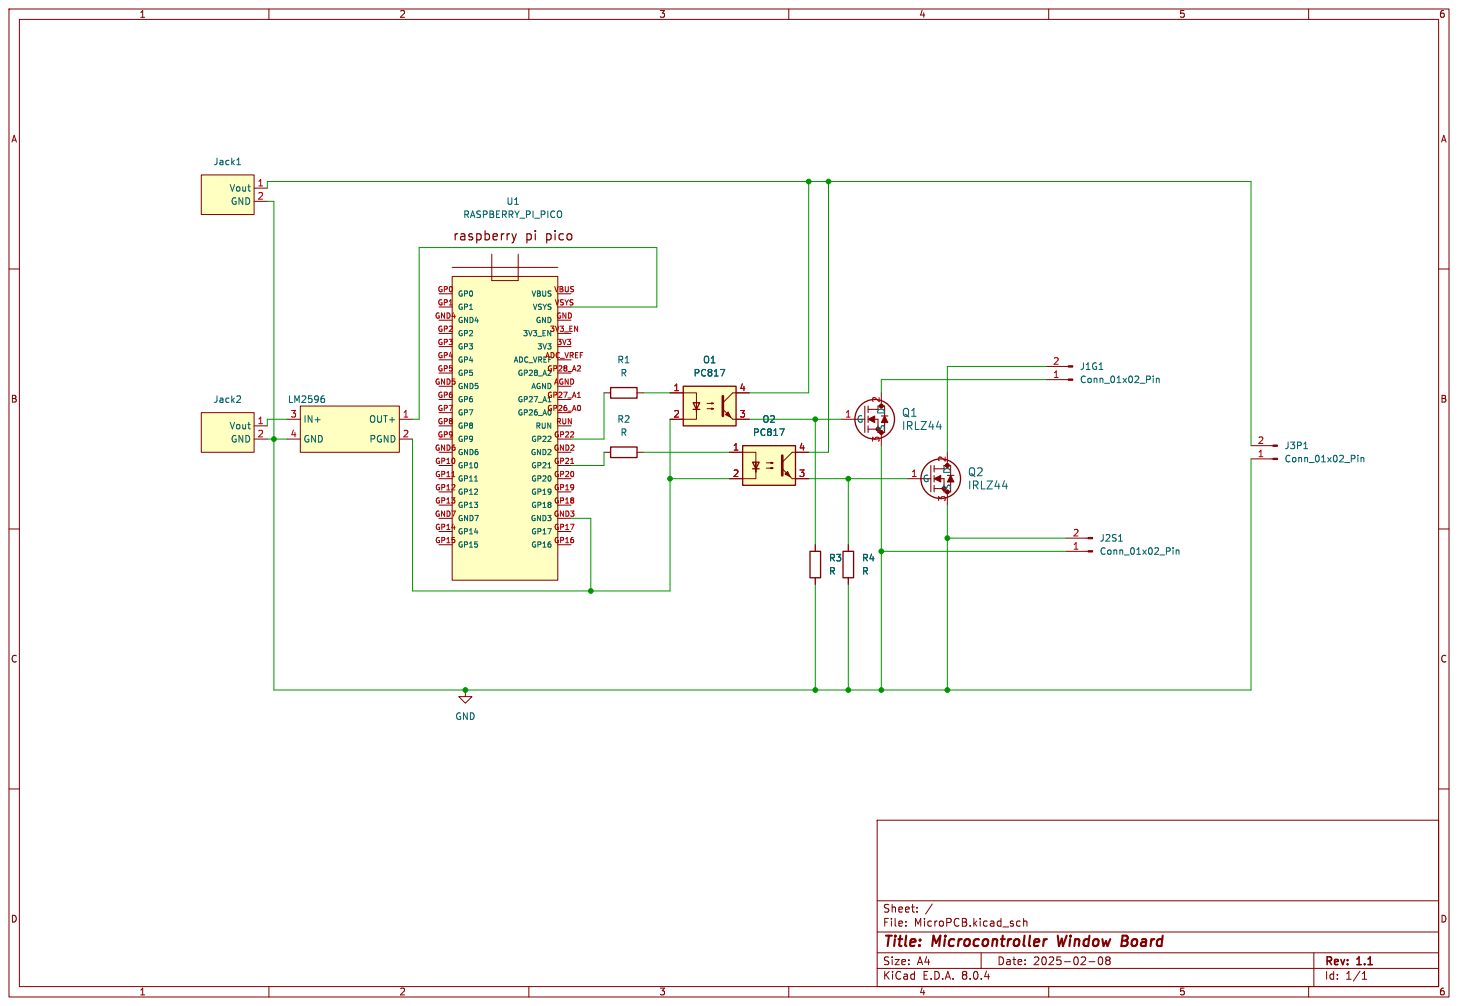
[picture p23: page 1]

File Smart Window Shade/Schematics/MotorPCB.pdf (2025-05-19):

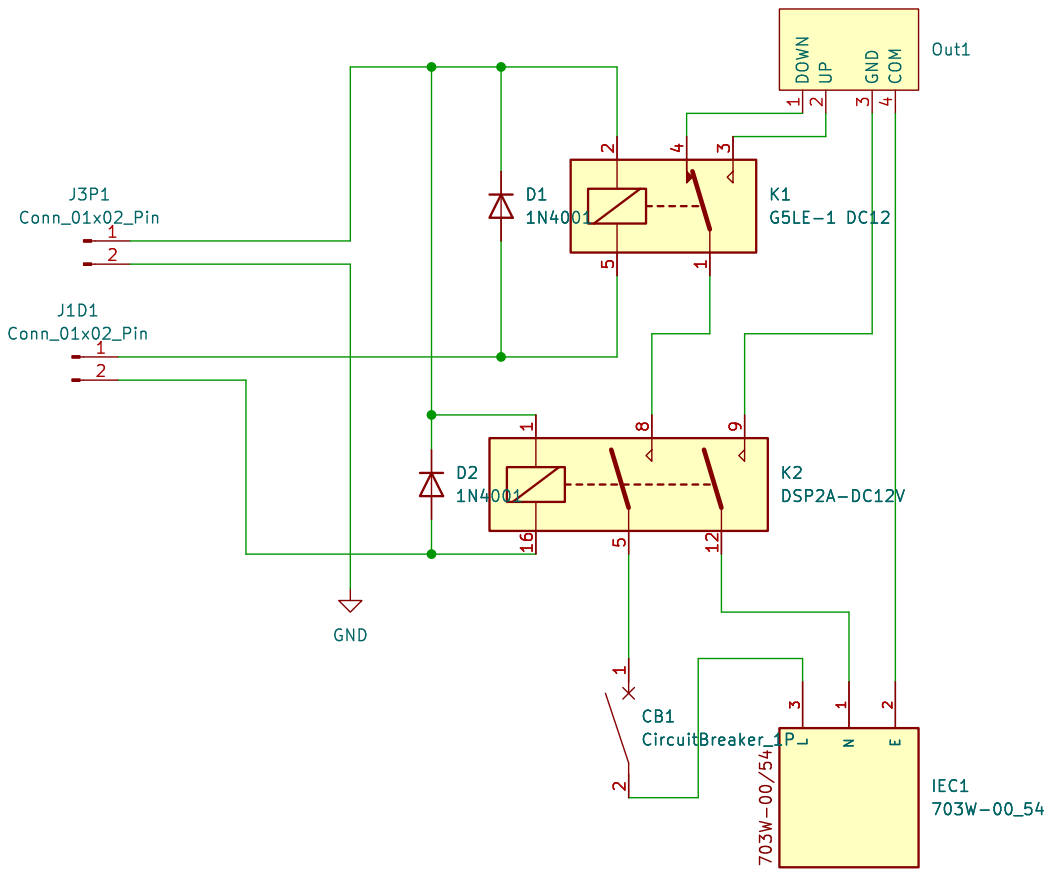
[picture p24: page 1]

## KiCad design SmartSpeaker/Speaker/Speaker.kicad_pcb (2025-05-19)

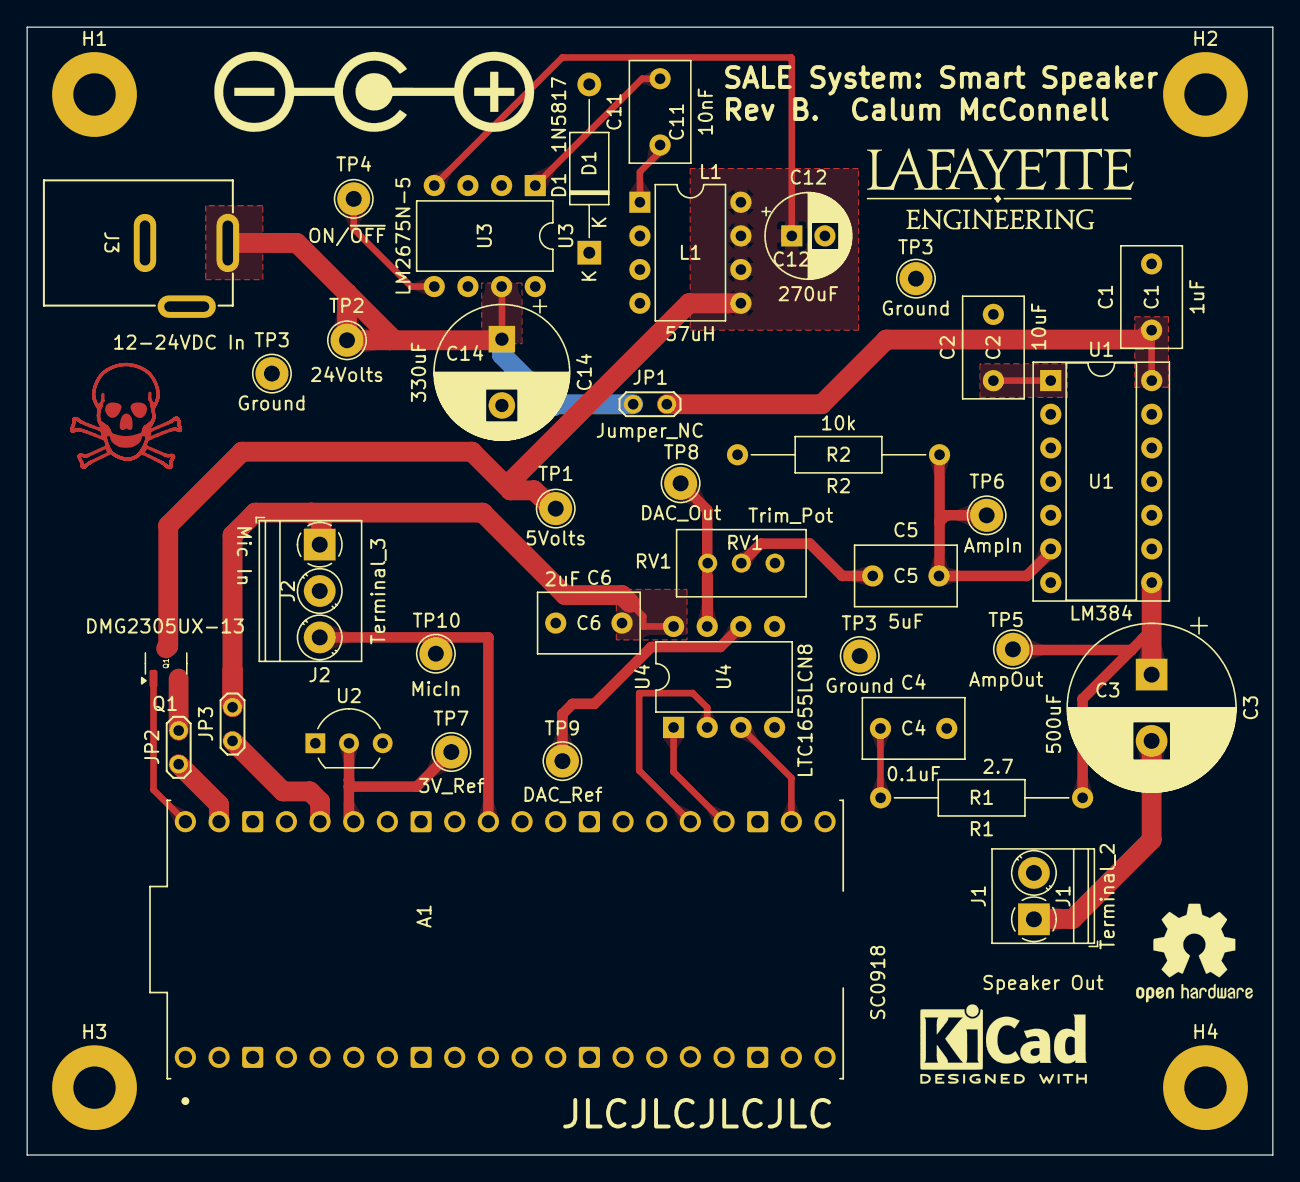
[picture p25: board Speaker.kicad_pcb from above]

Board: 2 copper layers, 94.0 x 85.1 mm, 42 parts (0 on the bottom side), 25 nets.

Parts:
A1: SC0918; MODULE_SC0918
C1: 1uF; C_Disc_D7.5mm_W4.4mm_P5.00mm
C2: 10uF; C_Disc_D7.5mm_W4.4mm_P5.00mm
C3: 500uF; CP_Radial_D12.5mm_P5.00mm
C4: 0.1uF; C_Disc_D7.5mm_W4.4mm_P5.00mm
C5: 5uF; C_Disc_D7.5mm_W4.4mm_P5.00mm
C6: 2uF; C_Disc_D7.5mm_W4.4mm_P5.00mm
C11: 10nF; C_Disc_D7.5mm_W4.4mm_P5.00mm
C12: 270uF; CP_Radial_D6.3mm_P2.50mm
C14: 330uF; CP_Radial_D10.0mm_P5.00mm
D1: 1N5817; D_A-405_P12.70mm_Horizontal
H1, H2, H3, H4: MountingHole_Pad; MountingHole_3.2mm_M3_Pad
J1: Terminal_2; TerminalBlock_Phoenix_PT-1,5-2-3.5-H_1x02_P3.50mm_Horizontal
J2: Terminal_3; TerminalBlock_Phoenix_PT-1,5-3-3.5-H_1x03_P3.50mm_Horizontal
J3: 54-00166; CONN3_54-00166_TEN
JP1, JP2, JP3: Jumper_NC; TestPoint_2Pads_Pitch2.54mm_Drill0.8mm
L1: 57uH; DIP-8_W7.62mm
Q1: DMG2305UX-13; SOT-23-3
R1: 2.7; R_Axial_DIN0207_L6.3mm_D2.5mm_P15.24mm_Horizontal
R2: 10k; R_Axial_DIN0207_L6.3mm_D2.5mm_P15.24mm_Horizontal
RV1: Trim_Pot; Potentiometer_Bourns_3296W_Vertical
TP1: 5Volts; TestPoint_THTPad_D2.5mm_Drill1.2mm
TP2: 24Volts; TestPoint_THTPad_D2.5mm_Drill1.2mm
TP3, TP3#2, TP3#3: Ground; TestPoint_THTPad_D2.5mm_Drill1.2mm
TP4: ON/~{OFF}; TestPoint_THTPad_D2.5mm_Drill1.2mm
TP5: AmpOut; TestPoint_THTPad_D2.5mm_Drill1.2mm
TP6: AmpIn; TestPoint_THTPad_D2.5mm_Drill1.2mm
TP7: 3V_Ref; TestPoint_THTPad_D2.5mm_Drill1.2mm
TP8: DAC_Out; TestPoint_THTPad_D2.5mm_Drill1.2mm
TP9: DAC_Ref; TestPoint_THTPad_D2.5mm_Drill1.2mm
TP10: MicIn; TestPoint_THTPad_D2.5mm_Drill1.2mm
U1: LM384; DIP-14_W7.62mm_Socket
U2: LM4040LP-3; TO-92_Inline_Wide
U3: LM2675N-5; DIP-8_W7.62mm
U4: LTC1655LCN8; DIP-8_W7.62mm

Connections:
/Adafruit_1713_Microphone/OUTPUT: A1.31 (GP26), J2.3, TP10.1
/AudioOut: C3.1, R1.1, TP5.1, U1.8
/Power_converter/5VOut: C12.1, L1.5, L1.6, L1.7, L1.8, Q1.3 (D), TP1.1, U3.4 (FB)
/Power_converter/VSwitch: C11.1, D1.1 (K), L1.1, L1.2, L1.3, L1.4, U3.8 (VSW)
/Power_converter/VoltageIn: C14.1, J3.1, JP1.1 (A), TP2.1, U3.7 (VIN)
/SpeakerOut: C3.2, J1.1
GND: A1.3 (GND), A1.8 (GND), A1.13 (GND), A1.18 (GND), A1.23 (GND), A1.28 (GND), A1.32 (GP27), A1.33 (AGND), A1.38 (GND), C1.2, C2.2, C4.2, C6.2, C12.2, C14.2, D1.2 (A), H1.1, H2.1, H3.1, H4.1, J1.2, J2.2, J3.3, R2.2, RV1.1, TP3.1, TP3#2.1, TP3#3.1, U1.2 (+), U1.3 (GND), U1.4 (GND), U1.5 (GND), U1.7 (GND), U1.10 (GND), U1.11 (GND), U1.12 (GND), U2.1 (NC), U2.3 (A), U3.6 (GND), U4.5 (GND)
unnamed: A1.36 (3V3_OUT), JP3.1 (A)
unnamed: A1.35 (ADC_VREF), TP7.1, U2.2 (K)
unnamed: A1.22 (GP17), U4.3 (~CS/LD)
unnamed: A1.24 (GP18), U4.1 (CLK)
unnamed: A1.25 (GP19), U4.2 (DIN)
unnamed: A1.40 (VBUS), Q1.1 (G)
unnamed: A1.39 (VSYS), JP2.1 (A)
unnamed: C4.1, R1.2
unnamed: C5.1, RV1.2
unnamed: C1.1, JP1.2 (B), U1.14 (VS)
unnamed: JP2.2 (B), Q1.2 (S)
unnamed: C5.2, R2.1, TP6.1, U1.6 (-)
unnamed: C2.1, U1.1 (BYPASS)
unnamed: C11.2, U3.1 (CB)
unnamed: TP4.1, U3.5 (ON/~OFF)
unnamed: TP9.1, U4.6 (REF)
unnamed: RV1.3, TP8.1, U4.7 (VOUT)
VDD: C6.1, J2.1, JP3.2 (B), U4.8 (VCC)

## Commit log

2025-04-24 Add ESPHome device configs to macrorepo
2025-05-05 Switched pin for protoboard, changed to button - Chris
2025-05-19 Raise SmartSpeaker to proper folder
    [12vTo5vRegulator.kicad_sch, Adafruit_Mic_Circity_1713.kicad_sch, LTC1655CN8_PBF.step, Speaker.kicad_pcb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]
2025-05-19 reorganized and added 3d print files
    [Bottom+V3.f3d, Bottom+V4.f3d, Hinge+Rods.f3d, Kick-Button+Combined+Visual.f3z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]
2025-05-19 Add SMD_05_19.aia to Smart Mobile Device
2025-05-19 add lastest speaker case designs
    [SmartSpeakerCaseTop.3mf, SmartSpeakerCase_Body.3mf]
